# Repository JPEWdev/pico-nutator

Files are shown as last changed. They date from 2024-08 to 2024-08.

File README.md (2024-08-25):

# pico-nutator

This repository contains the source code and KiCad Schematic and PCB for a Pico
Pi powered scientific rocker (e.g. a nutator). The machine is designed to mix
small quantities of liquid (i.e. test tubes) by gently rocking them back and
forth or around in circles.

This is for a homemade rocker that I built. While the one I built is just a
rocker and not actually a [nutator](https://en.wikipedia.org/wiki/Nutation),
the software and hardware design could be utilized with different mechanical
designs.

## Basic hardware design

The PCB routes power from a 12V power brick, through a power switch, then out
to a 3 pin connector. This connector goes to a commonly available L298N dual
H-bridge board. This stepper motor driver provide back 5V power, courtesy of an
on board linear regulator.

A Raspberry Pi Pico is the brains of the system. It has 4 motor outputs driven
via PWM to L298N motor controller board to drive the 2 poles of a stepper motor
using the dual H-bridge. These outputs are driven via PWM to ensure that the
motor does not exceed its rated current limit. In addition there is a motor
enable output pin which goes to the L298N to completely disable the H-bridge,
allowing the motor to spin freely. This is important because the stepper motor
will draw current when it is locked in place, wasting power. If the rocker is
not running and has no inputs for 60 seconds, it will go into "sleep mode" and
disable the H-bridge to save energy.

For input, there are 3 buttons; a Start/Stop button to start and stop the
motor, and an up and down button to increase or decrease the target RPM of the
motor. The target RPM can be changed while the motor is stopped, or running.
The software will also apply acceleration to the motor RPM, so that it smoothly
ramps up or down to the target RPM when starting or when the RPM has changed.
When changing speed, the display will show the percentage of the target speed
the motor is currently running at.

For display, the Pico Pi is connected to a Newhaven K3Z family 2x16 LCD.

Finally, a fan output is enabled when the motor is enabled to cool the L298N,
as it can get hot while running. The fan turns off in sleep mode.

The Schematic and PCB were designed in [KiCad](https://www.kicad.org/)

## Software

The software is written in C using the [Pico Pi SDK](https://www.raspberrypi.com/documentation/pico-sdk/).
An initial prototype was written in Python using
[CircuitPython](https://circuitpython.org/), however it had to be re-written in
C since the overhead and jitter in the Python code made it unable to get
precise timing on motor output pins, and thus it did not run smoothly,
especially at high RPM (e.g. above 30)

## Compiling and Installing

To build the software yourself first ensure that you have a suitable cross
compiler installed to compile for the Pico Pi (I used GCC, but presume Clang
would work also). First, the Pico Pi SDK must be fetched as a submodule using:

```shell
git submodule update --init --recursive
```

Next, make a build directory, configure it using `cmake`, and build using
`ninja` (using `ninja` is recommended, as it will result in a faster build of
the SDK):

```shell
mkdir build
cd build
cmake .. -GNinja
ninja
```

To load the software onto the Pico Pi, ensure it is not powered, then hold down
the `BOOTSEL` button while plugging it into the USB port of your computer. The
Pico Pi will show up as a removal USB drive. Copy the `nutator.bin` file to
this USB drive, and the Pico Pi will automatically reboot and start executing
the program.

## Final Assembly

Here is a picture of the final assembled rocker I built:
Rocker

And here is a close up of the electronics with the control board and H-bridge
labeled:
Control Electronics

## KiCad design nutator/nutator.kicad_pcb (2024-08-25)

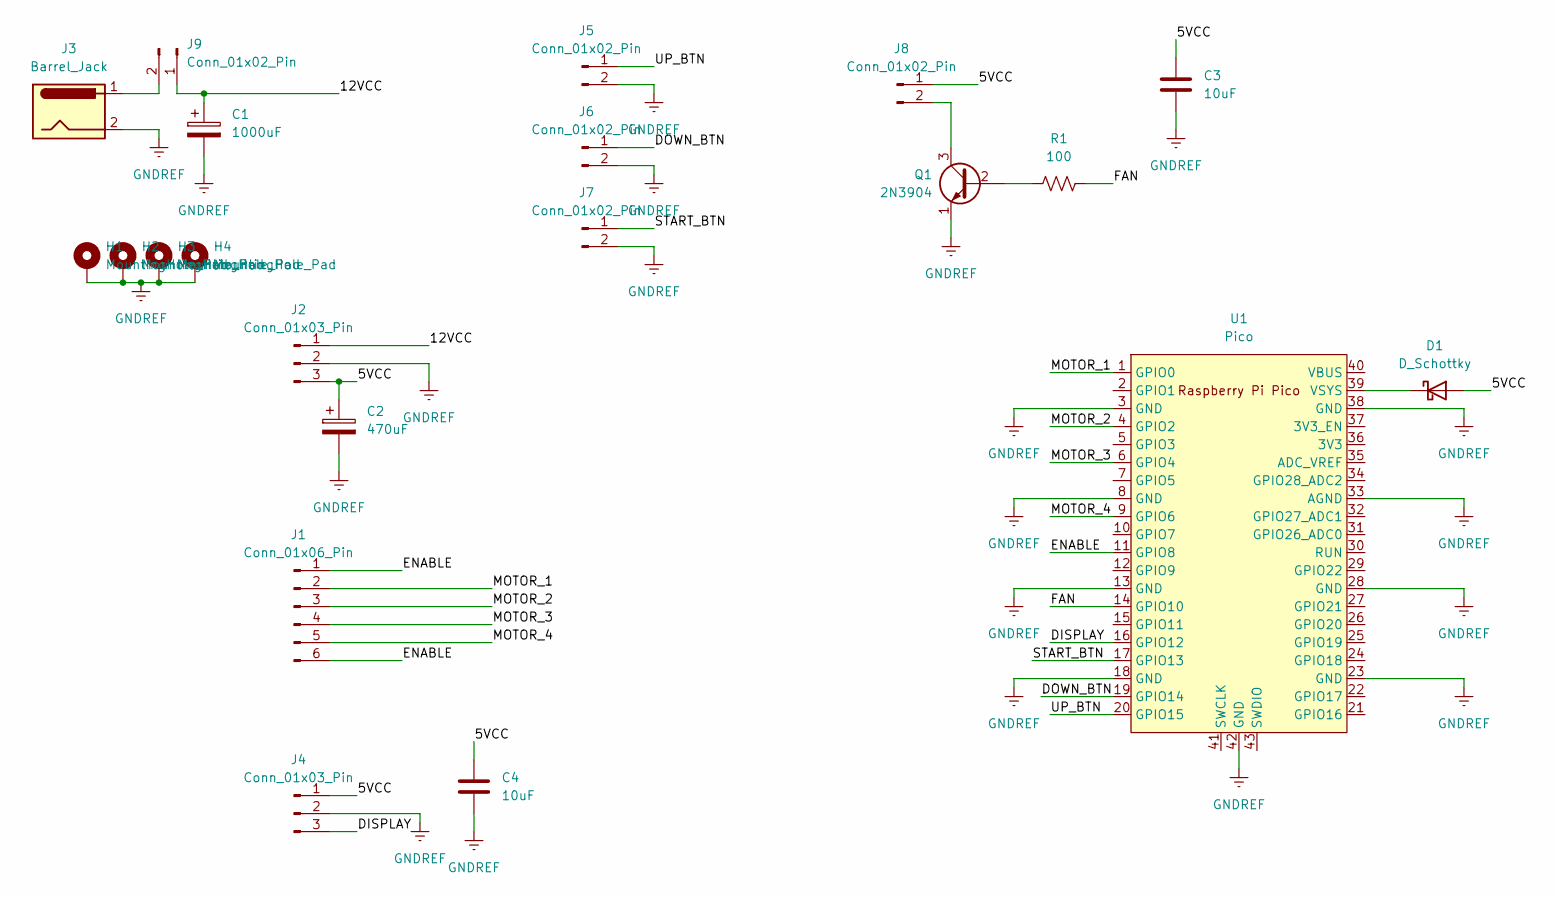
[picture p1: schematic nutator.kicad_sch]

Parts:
C1: 1000uF; CP_Radial_D8.0mm_P3.50mm
C2: 470uF; CP_Radial_D8.0mm_P3.50mm
C3, C4: 10uF; C_0603_1608Metric_Pad1.08x0.95mm_HandSolder
D1: D_Schottky; D_SOD-123F
H1, H2, H3, H4: MountingHole_Pad; MountingHole_3.2mm_M3_ISO7380_Pad
J1: Conn_01x06_Pin; PinHeader_1x06_P2.54mm_Vertical
J2, J4: Conn_01x03_Pin; PinHeader_1x03_P2.54mm_Vertical
J3: Barrel_Jack; BarrelJack_CUI_PJ-036AH-SMT_Horizontal
J5, J6, J7, J8, J9: Conn_01x02_Pin; PinHeader_1x02_P2.54mm_Vertical
Q1: 2N3904; TO-92_Inline
R1: 100; R_0603_1608Metric_Pad0.98x0.95mm_HandSolder
U1: Pico; RPi_Pico_SMD_TH

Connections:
/5VCC: C2.1, C3.1, C4.1, D1.2 (A), J2.3, J4.1, J8.1
/12VCC: C1.1, J2.1, J9.1
/DISPLAY: J4.3, U1.16 (GPIO12)
/DOWN_BTN: J6.1, U1.19 (GPIO14)
/ENABLE: J1.1, J1.6, U1.11 (GPIO8)
/FAN: R1.2, U1.14 (GPIO10)
/MOTOR_1: J1.2, U1.1 (GPIO0)
/MOTOR_2: J1.3, U1.4 (GPIO2)
/MOTOR_3: J1.4, U1.6 (GPIO4)
/MOTOR_4: J1.5, U1.9 (GPIO6)
/START_BTN: J7.1, U1.17 (GPIO13)
/UP_BTN: J5.1, U1.20 (GPIO15)
GNDREF: C1.2, C2.2, C3.2, C4.2, H1.1, H2.1, H3.1, H4.1, J2.2, J3.2, J4.2, J5.2, J6.2, J7.2, Q1.1 (E), U1.3 (GND), U1.8 (GND), U1.13 (GND), U1.18 (GND), U1.23 (GND), U1.28 (GND), U1.33 (AGND), U1.38 (GND), U1.42 (GND)
unnamed: D1.1 (K), U1.39 (VSYS)
unnamed: J8.2, Q1.3 (C)
unnamed: J3.1, J9.2
unnamed: Q1.2 (B), R1.1

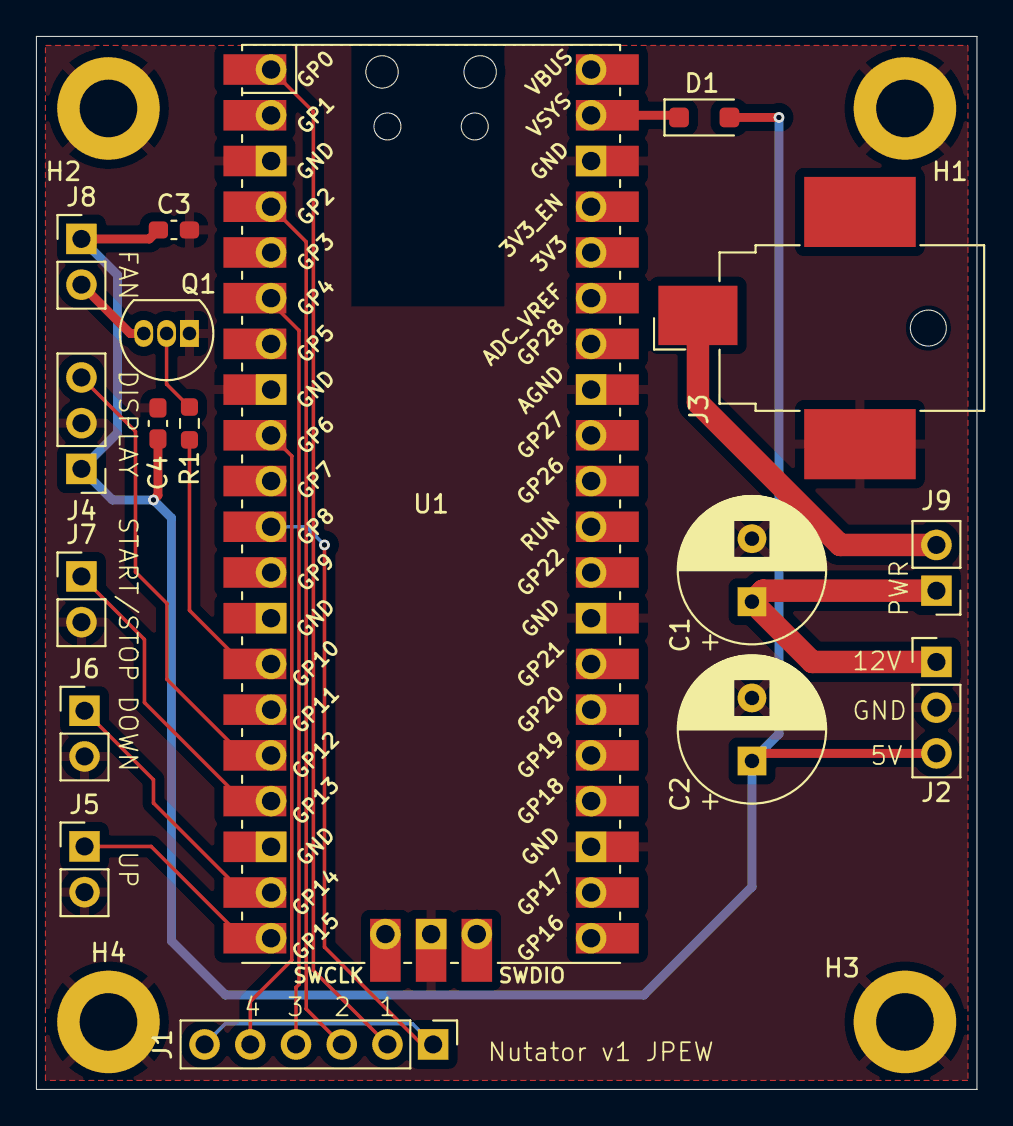
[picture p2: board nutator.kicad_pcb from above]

Board: 2 copper layers, 52.2 x 58.5 mm, 21 parts (0 on the bottom side), 17 nets.

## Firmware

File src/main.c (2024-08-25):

/*
 * SPDX-License-Identifier: MIT
 *
 * Copyright (c) 2024 Joshua Watt
 */
#include <inttypes.h>
#include <stdio.h>

#include "button.h"
#include "hardware/pwm.h"
#include "nhd-k3z.h"
#include "persist.h"
#include "pico/stdlib.h"
#include "stepper-motor.h"

#define VERSION "1.0"

#define MAX_RPM (60)
#define RPM_STEP (5)
#define STEPS_PER_REV (200)
#define SLEEP_TIMEOUT_US (60 * 1000000)

/*
 * Frequency is high so that the stepper motor is (more or less) not audible
 * when holding
 */
#define MOTOR_FREQUENCY (15000)

/*
 * Power supply is 12V, the motor is rated for 1.5 Amps max, with a resistance
 * of 2.3 Ohms. In an ideal world, this would normally be a 28% duty cycle,
 * however the frequency of our PWM is quite a bit above the cutoff frequency
 * of the motor (4 mH inductance, cutoff is 91 Hz), so lot of attenuation is
 * happening, and there is a pretty non-linear response to the duty cycle
 * because of this.
 *
 * As such, this was determined empirically, mostly by checking if the stepper
 * motor driver was too hot to touch
 */
#define MOTOR_DUTY_CYCLE (40)

#define MOTOR_ACCEL (60)

#define LED_PIN (25)

#define ARRAY_COUNT(arr) (sizeof(arr) / sizeof(arr[0]))

/*
 * Motor uses even pins so that each can has its own independent PWM. This is
 * in case I want to do micro-stepping some day
 */
static const unsigned int motor_pins[] = {0, 4, 2, 6};

/*
 * Motor enable pin is also even in case we want to independently PWM it
 */
#define MOTOR_ENABLE_PIN (8)

/*
 * Fan pin is also even in case we want to independently PWM it
 */
#define FAN_PIN (10)

#define DISPLAY_PIN (12)
#define DISPLAY_UART (uart0)

#define START_STOP_BTN_PIN (13)
#define DOWN_BTN_PIN (14)
#define UP_BTN_PIN (15)

static struct button* make_button(int pin) {
    struct button* b = button_create(pin, true, 35);
    gpio_pull_up(pin);
    button_set_repeat(b, 1000, 500);
    return b;
}

bool run = false;
uint64_t run_time_start = 0;
bool sleeping = false;
struct nhdk3z* display;
struct stepper* motor;

struct persist persist;

struct hms {
    unsigned int hours;
    unsigned int minutes;
    unsigned int seconds;
};

static struct hms us_to_hms(uint64_t us) {
    struct hms result;

    result.hours = us / (1000000ull * 60 * 60);
    result.minutes = (us / (1000000ull * 60)) % 60;
    result.seconds = (us / 1000000ull) % 60;

    return result;
}

static void set_target_rpm(unsigned int new_rpm) {
    new_rpm = MAX(new_rpm, RPM_STEP);
    new_rpm = MIN(new_rpm, MAX_RPM);

    persist.target_rpm = new_rpm;
    if (run) {
        stepper_set_rpm(motor, persist.target_rpm);
    }

    printf("Target RPM is now %" PRIu32 "\n", persist.target_rpm);
}

static void update_display() {
    if (sleeping) {
        return;
    }

    nhdk3z_clear(display);
    nhdk3z_home(display);
    if (run) {
        struct hms hms = us_to_hms(time_us_64() - run_time_start);

        nhdk3z_printf(display, "Running %u:%02u:%02u", hms.hours, hms.minutes,
                      hms.seconds);
    } else {
        nhdk3z_write(display, "Stopped");
    }
    nhdk3z_set_cursor(display, 0x40);
    nhdk3z_printf(display, "RPM %d", persist.target_rpm);
    if (run) {
        unsigned int actual_rpm = stepper_get_actual_rpm(motor);
        if (actual_rpm && actual_rpm != persist.target_rpm) {
            nhdk3z_printf(display, " (%d%%)",
                          100 * actual_rpm / persist.target_rpm);
        }
    }
}

static void set_sleep(bool sleep) {
    if (sleeping == sleep) {
        return;
    }

    sleeping = sleep;

    stepper_enable(motor, !sleeping);
    if (sleeping) {
        nhdk3z_set_brightness(display, 1);
        gpio_put(FAN_PIN, 0);
    } else {
        nhdk3z_set_brightness(display, 8);
        stepper_hold(motor);
        gpio_put(FAN_PIN, 1);
        update_display();
    }
}

static uint32_t pwm_set_freq_duty(unsigned int slice_num, unsigned int chan,
                                  uint32_t frequency, int duty) {
    uint32_t clock = 125000000;
    uint32_t divider16 =
        clock / frequency / 4096 + (clock % (frequency * 4096) != 0);
    if (divider16 / 16 == 0) {
        divider16 = 16;
    }
    uint32_t wrap = clock * 16 / divider16 / frequency - 1;
    pwm_set_clkdiv_int_frac(slice_num, divider16 / 16, divider16 & 0xF);
    pwm_set_wrap(slice_num, wrap);
    pwm_set_chan_level(slice_num, chan, wrap * duty / 100);
    return wrap;
}

int main() {
    stdio_init_all();
    gpio_init(LED_PIN);
    gpio_set_dir(LED_PIN, GPIO_OUT);
    gpio_put(LED_PIN, 1);
    printf("Booting...");
    /* Wait for display to power up */
    sleep_ms(1000);
    read_persist(&persist);

    /* Buttons */
    struct button* up_button = make_button(UP_BTN_PIN);
    struct button* down_button = make_button(DOWN_BTN_PIN);
    struct button* start_stop_button = make_button(START_STOP_BTN_PIN);

    /* Fan */
    gpio_init(FAN_PIN);
    gpio_set_dir(FAN_PIN, GPIO_OUT);
    gpio_put(FAN_PIN, 0);

    /* Motor */
    /*
     * The motor is driven in half-step mode. This results in uneven torque and
     * lower average torque than dual phase stepping, since each alternating
     * step uses either 1 or 2 phases of the motor. However, the motor runs
     * much smoother since it effectively doubles the number of steps
     */
    motor = stepper_create(STEPS_PER_REV, MAX_RPM, STEPPER_MODE_HALF_STEP,
                           MOTOR_ENABLE_PIN);

    uint32_t pwm_mask = 0;
    for (int i = 0; i < ARRAY_COUNT(motor_pins); i++) {
        unsigned int slice_num = pwm_gpio_to_slice_num(motor_pins[i]);
        unsigned int chan = pwm_gpio_to_channel(motor_pins[i]);
        pwm_set_freq_duty(slice_num, chan, MOTOR_FREQUENCY, MOTOR_DUTY_CYCLE);
        stepper_add_pin(motor, motor_pins[i], true);
        pwm_mask |= 1 << slice_num;
    }
    pwm_set_mask_enabled(pwm_mask);

    /* Display */
    display = nhdk3z_create(DISPLAY_UART);
    gpio_set_function(DISPLAY_PIN, GPIO_FUNC_UART);
    nhdk3z_set_baud(display, NHDK3Z_BAUD_57600);

    nhdk3z_set_display_on(display, true);
    nhdk3z_set_contrast(display, 50);
    nhdk3z_set_brightness(display, 8);
    nhdk3z_set_cursor_blink(display, false);
    nhdk3z_set_cursor_underline(display, false);
    nhdk3z_clear(display);
    nhdk3z_home(display);
    nhdk3z_printf(display, "Version %s", VERSION);
    sleep_ms(2000);

    stepper_set_accel(motor, MOTOR_ACCEL, RPM_STEP);
    stepper_enable(motor, true);
    stepper_hold(motor);
    update_display();
    gpio_put(FAN_PIN, 1);

    uint64_t sleep_start = time_us_64();
    int run_time_sec = 0;

    while (true) {
        uint64_t now = time_us_64();
        bool redraw = false;

        if (!run && !sleeping && now >= sleep_start + SLEEP_TIMEOUT_US) {
            set_sleep(true);
        }

        /*
         * Redraw if running and the seconds have changed
         */
        if (run) {
            struct hms hms = us_to_hms(now - run_time_start);
            if (hms.seconds != run_time_sec) {
                redraw = true;
                run_time_sec = hms.seconds;
            }
        }

        gpio_put(LED_PIN, stepper_update(motor) ? 1 : 0);
        button_update(up_button);
        button_update(down_button);
        button_update(start_stop_button);

        if (sleeping) {
            if (button_up(up_button) || button_up(down_button) ||
                button_up(start_stop_button)) {
                set_sleep(false);
                sleep_start = now;
            }
        } else {
            if (button_repeat(up_button)) {
                set_target_rpm(persist.target_rpm + RPM_STEP);
                sleep_start = now;
                redraw = true;
            }

            if (button_repeat(down_button)) {
                set_target_rpm(persist.target_rpm - RPM_STEP);
                sleep_start = now;
                redraw = true;
            }

            if (!run && button_is_pressed(start_stop_button) &&
                button_current_duration_us(start_stop_button) >= 4000000) {
                nhdk3z_clear(display);
                nhdk3z_home(display);
                nhdk3z_write(display, "Sleeping...");
                sleep_ms(1000);
                set_sleep(true);
                while (!button_up(start_stop_button)) {
                    button_update(start_stop_button);
                }
            } else if (button_up(start_stop_button)) {
                run = !run;
                write_persist(&persist);
                if (run) {
                    stepper_set_rpm(motor, persist.target_rpm);
                    run_time_start = now;
                    run_time_sec = 0;
                } else {
                    stepper_set_rpm(motor, 0);
                }
                sleep_start = now;
                redraw = true;
            }
        }

        if (redraw) {
            update_display();
        }
    }

    return 0;
}

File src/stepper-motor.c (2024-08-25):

/*
 * Stepper motor driver for Pico Pi
 *
 * SPDX-License-Identifier: MIT
 *
 * Copyright (c) 2024 Joshua Watt
 */
#include "stepper-motor.h"

#include <stdbool.h>
#include <stdint.h>
#include <stdlib.h>

#include "pico/stdlib.h"

#define US_PER_SEC (1000000ull)
#define US_PER_MIN (60 * US_PER_SEC)

#define MIN_RPM (1ull)

struct stepper {
    unsigned int steps_per_rev;
    unsigned int max_rpm;
    enum stepper_mode mode;
    unsigned int mask;
    unsigned int half_mask;
    unsigned int target_rpm;
    unsigned int accel_rpm_per_sec;
    int enable_pin;
    size_t num_pins;
    struct {
        unsigned int pin;
        bool is_pwm;
    }* pins;
    uint64_t last_step;
    uint64_t us_per_step_target;
    uint64_t us_per_step;
    uint64_t us_accel;
    uint64_t max_us_per_step;
    uint64_t last_accel_step;
    uint64_t step_count;
};

static uint64_t rpm_to_step_us(struct stepper const* s, unsigned int rpm) {
    return US_PER_MIN / ((uint64_t)rpm * s->steps_per_rev);
}

static void update(struct stepper const* s) {
    uint32_t mask = 0;
    uint32_t value = 0;
    for (size_t i = 0; i < s->num_pins; i++) {
        mask |= 1 << s->pins[i].pin;

        if (((s->mask | s->half_mask) >> i) & 0x1) {
            if (s->pins[i].is_pwm) {
                gpio_set_function(s->pins[i].pin, GPIO_FUNC_PWM);
            } else {
                value |= 1 << s->pins[i].pin;
            }
        } else if (s->pins[i].is_pwm) {
            gpio_set_function(s->pins[i].pin, GPIO_FUNC_SIO);
        }
    }
    gpio_put_masked(mask, value);
}

static uint32_t step_mask(uint32_t mask, bool forward, size_t num_pins) {
    if (forward) {
        if (mask & 0x1) {
            mask |= (1 << num_pins);
        }
        mask >>= 1;
    } else {
        mask <<= 1;
        if (mask & (1 << num_pins)) {
            mask |= 1;
        }
    }
    mask &= (1 << num_pins) - 1;

    return mask;
}

static void step(struct stepper* s, bool forward) {
    if (!s->mask) {
        stepper_hold(s);
        return;
    }

    /*
     * For half step, move the main mask on odd steps, and the half mask on
     * even steps
     */
    if (s->mode != STEPPER_MODE_HALF_STEP || (s->step_count & 1)) {
        s->mask = step_mask(s->mask, forward, s->num_pins);
    } else {
        s->half_mask = step_mask(s->half_mask, forward, s->num_pins);
    }

    s->step_count++;
    update(s);
}

struct stepper* stepper_create(unsigned int steps_per_rev, unsigned int max_rpm,
                               enum stepper_mode mode, int enable_pin) {
    struct stepper* s = calloc(1, sizeof(*s));
    s->steps_per_rev = steps_per_rev;
    if (mode == STEPPER_MODE_HALF_STEP) {
        s->steps_per_rev *= 2;
    }
    s->max_rpm = max_rpm;
    s->mode = mode;
    s->enable_pin = enable_pin;
    if (enable_pin >= 0) {
        gpio_init(enable_pin);
        gpio_set_dir(enable_pin, GPIO_OUT);
        gpio_put(enable_pin, 0);
    }
    return s;
}

void stepper_free(struct stepper* s) {
    for (size_t i = 0; i < s->num_pins; i++) {
        gpio_deinit(s->pins[i].pin);
    }
    if (s->enable_pin >= 0) {
        gpio_deinit(s->enable_pin);
    }
    free(s->pins);
    free(s);
}

void stepper_add_pin(struct stepper* s, unsigned int pin, bool is_pwm) {
    s->pins = realloc(s->pins, sizeof(*s->pins) * (s->num_pins + 1));
    s->pins[s->num_pins].pin = pin;
    s->pins[s->num_pins].is_pwm = is_pwm;
    s->num_pins++;

    gpio_init(pin);
    gpio_set_dir(pin, GPIO_OUT);
    gpio_put(pin, 0);
}

void stepper_set_accel(struct stepper* s, unsigned int rpm_per_sec,
                       unsigned int min_rpm) {
    if (rpm_per_sec == 0) {
        s->us_accel = 0;
    } else {
        s->us_accel = rpm_to_step_us(s, rpm_per_sec * 60);
        s->max_us_per_step = rpm_to_step_us(s, min_rpm);
    }
}

void stepper_step(struct stepper* s, bool forward) {
    step(s, forward);
    s->last_step = time_us_64();
    s->last_accel_step = s->last_step;
}

bool stepper_update(struct stepper* s) {
    uint64_t now = time_us_64();

    if (s->us_accel) {
        if (s->us_per_step_target == 0 &&
            (s->us_per_step == s->max_us_per_step || s->us_per_step == 0)) {
            s->us_per_step = 0;
        } else if (s->us_per_step_target != 0 && s->us_per_step == 0) {
            s->us_per_step = s->max_us_per_step;
        } else {
            if (now >= s->last_accel_step) {
                int num_steps = (now - s->last_accel_step) / s->us_accel;
                int64_t target = s->us_per_step_target ? s->us_per_step_target
                                                       : s->max_us_per_step;

                if (s->us_per_step < target) {
                    s->us_per_step =
                        MIN((int64_t)s->us_per_step + num_steps, target);
                } else if (s->us_per_step > target) {
                    s->us_per_step =
                        MAX((int64_t)s->us_per_step - num_steps, target);
                }

                s->last_accel_step += s->us_accel * num_steps;
            }
        }
    } else {
        s->us_per_step = s->us_per_step_target;
    }

    if (!s->us_per_step) {
        return false;
    }

    if (now >= s->last_step) {
        int num_steps = (now - s->last_step) / s->us_per_step;
        if (num_steps) {
            step(s, true);
            s->last_step += s->us_per_step;
        }

        return num_steps > 1;
    }
    return false;
}

void stepper_brake(struct stepper* s) {
    s->mask = 0;
    s->half_mask = 0;
    update(s);
}

void stepper_hold(struct stepper* s) {
    switch (s->mode) {
        case STEPPER_MODE_WAVE:
            s->mask = 0x1;
            s->half_mask = 0x0;
            break;

        case STEPPER_MODE_DUAL_PHASE:
            s->mask = 0x3;
            s->half_mask = 0x0;
            break;

        case STEPPER_MODE_HALF_STEP:
            /*
             * Both masks must start on the same pin since it is random which
             * one will advance first
             */
            s->mask = 0x1;
            s->half_mask = 0x1;
            break;
    }
    update(s);
}
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

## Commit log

2024-08-25 Initial Implementation
    [nutator.kicad_pcb, nutator.kicad_sch]
2024-08-25 README.md: Add images
    Adds images of the final assembled rocker to the README.md
